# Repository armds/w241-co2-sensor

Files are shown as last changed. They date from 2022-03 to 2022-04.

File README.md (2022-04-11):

# Intro
This is the repository for code and documents for the sensor we built for our w241 - Causal Inference class project, Spring 2022.

It should give you enough information to build one of these sensors should you so desire.

# Components required

## Arduino components

- [Sparkfun Qwiic Pro Micro USB-C](https://www.sparkfun.com/products/15795?_ga=2.264082766.31748102.1649701746-416199447.1644960318)  This is the Arduino mainboard we used.  Other boards can be used instead, but the CAD expects this one and the other boards are Qwiic connectors so it should support this.
- [Sparkfun CCS811/BME280 (Qwiic) Environmental Combo Breakout](https://www.sparkfun.com/products/14348?_ga=2.264082766.31748102.1649701746-416199447.1644960318) This board is the heart of the sensor.  Once calibrated (see notes below) it will measure temperature, humidity, air pressure, CO2 and TVOC.
- [SparkFun Real Time Clock Module](https://www.sparkfun.com/products/14558?_ga=2.62422382.31748102.1649701746-416199447.1644960318)  This chip is required to have a continuous sense of time.  Without it the device's only sense is seconds since power cycle.  Nominally that would work for an experiment, but in practice the power tends to flicker and cause frequent resets.
- [Sparkfun Qwiic OpenLog](https://www.sparkfun.com/products/15164?_ga=2.264082766.31748102.1649701746-416199447.1644960318)  This is required if you want to operate your device away from computer and persist the data.  Hypohtetically you could instead use a wifi card and configure it write to the cloud, but we wanted to use it in locations remote from where it was developed so could not guarenee connectivity.

## Other components
- [Battery Pack](https://www.amazon.com/gp/product/B08T8TDS8S)  The device does not care what its power supply is.  It can be powered off a computer, or any portable USB power supply. That said the CAD provided exactly matches these batteries, and using any other will require a new case.

- [USB cables ](https://www.amazon.com/gp/product/B096VYVR17) Again any USB cables can be used.  Our battery only has Micro USB and USB A, and the CPU needs USB-C.  With the case space constraints we went with these, and again, the CAD expects it.

- [3x Qwiic cables](https://www.sparkfun.com/products/17260) These aren't special, you just need 3 Qwiic cables per sensor, get what works for you.

# CAD for case and cover

If you are using all the same parts as us, you can use the STL files in the *Case STL* directory to just print them.  Hopefully they work for you.  The spaces are intentionally designed to be a tight fit for the cards, and they are all subtily different shapes so will only work exactly in the configuration shown below.  They may be quite snug, so be firm but gentile pushing them in.

Its also possible that the fit between case and cover is either too loose or too tight.  For loose (our case) use a few pieces of thin tape to fill the gaps so they are snug.

If they really don't fit, or you want to change the configuration or battery, the [Onshape CAD Project](https://cad.onshape.com/documents/a2fdd6d62e2931dea2922d15/w/b632312d6c9ec3a2012bce3f/e/c36cc9c0a84920fe10cffbab) is public. You will likely need to make an Onshape account, and then can copy the files and edit them.

# Assembly
Blow are what they should look like open, with cards installed (yes they have to go in these spots!), and with the covers on.  They are fairly inconsipcuous with covers, but the lights inside have occasionally cought folks' attention.

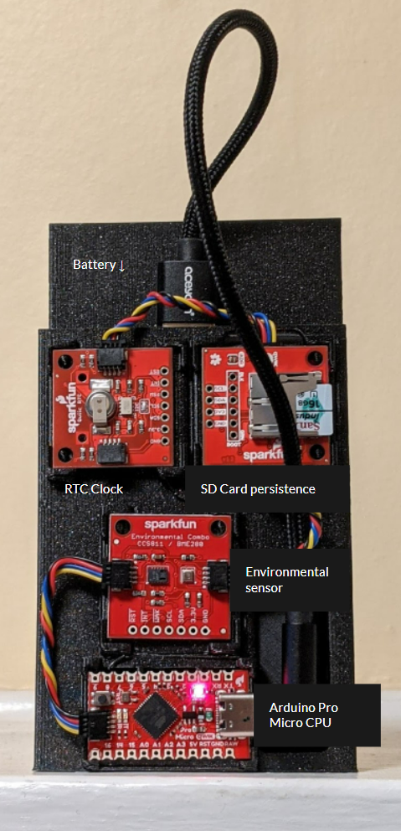
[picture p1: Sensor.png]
Image of case with cards properlly aranged


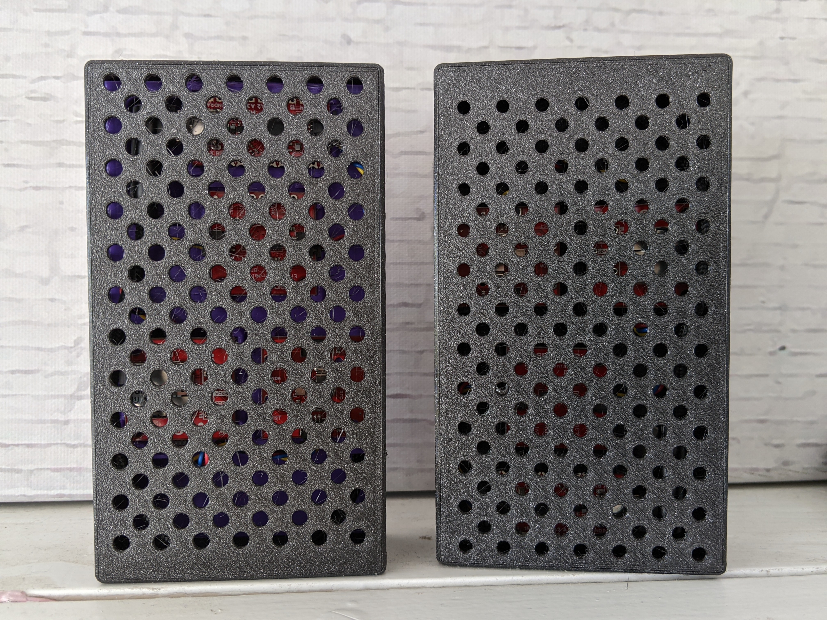
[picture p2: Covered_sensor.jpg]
Sensors with covers on


# Code for device

The code for the devices is in this repository in the *timed_sensor* directory.  The *base_sensor* will give you an earlier version that didn't have a persistant clock.

Use any tutorial on using the Arduino IDE to install the code on the device.  Its fairly simple, so SparkFun's basic tutorial is fine.

Code in this repo is based on the example code provided by SparkFun for each card.  They are a good reference for understanding it for modification.

## Time setting

One important issue is setting the clock chip.  The way it is set is when you push the code to the device it will set the device's time to the time at which the IDE was started.   So if you take 10 minutes from start to upload your clock will be off by that amount.  So get your code perfect, restart the IDE, and push.  Do this cycle for each device, and know they will be off by some degree due to the time this delay.  Sorry for the hassle, it is regretable!

Additionally our devices were built in one time zone, and deployed in another, so there is a 3 hour timezone correction built into the code, which may not be needed for all applications.

# Caviats for use

There are a few execution requirements to ensure you get an accurate atospheric measurements.

## Sensor Calibration

The first caveat is the sensors need to be calibrated at rest in a stable environment before starting to collect data.  The Environment chip has both the temperature sensor and the air sensor in close proximity.  At operating temperature the environmental chip can generate significant heat (up to 15 deg).  The temperature is one of the inputs for the CO2 calibration, so this temperature increase will make the measurements in accurate.  To compensate for this the device records its temperature at power up, and after 20 minutes will take the accumulated temperature change and subtract that from all subsequent measurements for calibration. In addition the plastic of the case and the battery can hold heat that messes this up.

This means for best performance when not in use you should to hold all devices in the same place, ideally not indoors, so the residual temperature is close to outdoors.  Additionally you should plug them in 20 minutes in advance, and keep them in a stabile temperature location.  So that that calibration constant is not picking up additional effects. 

Best practice would be to keep them outside, or in a cool garage, plug them in a half hour before you will deploy them, and minimize heat accumulation en route.

## Operating limits

These are prototype devices so are not environmentally secured.  In particular they are not robust to rain, so need to be placed  someplace under shelter.  Additionally direct sunlight can increase both measured temperature and CO2.  So both devices should be deployed with the same sun exposure, ideally shaddowed.

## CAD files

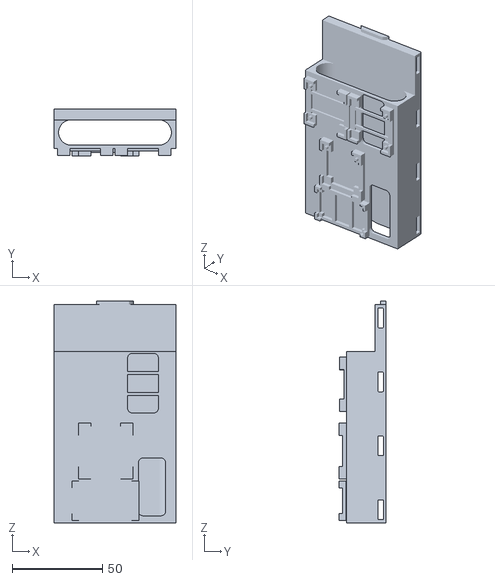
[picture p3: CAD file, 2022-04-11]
Case STLs/Battery and card holder.stl
67.5 x 26.0 x 123.0

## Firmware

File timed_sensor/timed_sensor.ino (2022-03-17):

/******************************************************************************
  Reads information from an evironmental sensor and writes an hourly csv file
  with environmental data.

  Boards expected:

  - Sparkfun Qwiic Pro Micro USB-C
  - Sparkfun CCS811/BME280 (Qwiic) Environmental Combo Breakout
  - Sparkfun Qwiic OpenLog
  - SparkFun Real Time Clock Module

  Libraries required:
   http://librarymanager/All#SparkFun_CCS811
   http://librarymanager/All#SparkFunBME280
   https://www.arduinolibraries.info/libraries/spark-fun-qwiic-open-log
   http://librarymanager/All#SparkFun_RV1805

 Author: Anne Marshal 
 Copyright: 2022
******************************************************************************/
#include <Wire.h>

#include "SparkFunCCS811.h" 
#include "SparkFunBME280.h"
#include "SparkFun_Qwiic_OpenLog_Arduino_Library.h"
#include "SparkFun_RV1805.h"

#define CCS811_ADDR 0x5B //Default I2C Address for the sensor
//#define CCS811_ADDR 0x5A //Alternate I2C Address

CCS811 myCCS811(CCS811_ADDR);
BME280 myBME280;
OpenLog myLog; //Create instance
RV1805 rtc;
OpenLog dataLog;

float tempCorrectionC = 0;
float tempCorrectionF = 0;
boolean correctionSet = false;
float startTempC;
float startTempF;

// How long to wait for temperature stabilization for correction term, normally 20
float delayMinutes = 20;

// sleep tolerance, how old a calibration use stamp can be for us to still use it.
float tolMinutes = 10;

// Name of calibration timestamp file
String calibrationTimeStampFile = "calstamp.txt";

// set this to either B or W depending on which sensor is being written to
// is only used for output CSV filenames
char sensorId = 'P';

// if we need to set the clock chip, this will set it to the time the IDE started
// then add 3 hours to adjust to EST time.  Don't do this after 9pm thought, 'cause its not smart!
// unless the chip has crashed for a while, it should seldom need to have the clock set.
boolean setClock = false;

// desired interval between samples in seconds
unsigned int secsBetweenSamples = 5;

// interval between calibration file writes
unsigned int secsBetweenCalibWrites = 120;


// string buffers like to be global, because memory is a thing
char fCorr[10];
char cCorr[10];
char calibuf[30];
char calibuf2[30];     

// Globalize frequently used vars for faster loops
unsigned int loopStartTime;
String currentTime;

   
void setup()
{
  Serial.begin(9600);

  Wire.begin(); //Initialize I2C
  myLog.begin(); //Open connection to OpenLog (no pun intended)

  // initialize clock
   if (rtc.begin() == false) {
    Serial.println("Something went wrong, check wiring");
  }

  //Use the time from the Arduino compiler (build time) to set the RTC
  //Keep in mind that Arduino does not get the new compiler time every time it compiles.
  //to ensure the proper time is loaded, open up a fresh version of the IDE and load the sketch.
  rtc.set24Hour();
  if (setClock) {
    if (rtc.setToCompilerTime() == false) {
      Serial.println("Something went wrong setting the time");
    }

    rtc.updateTime();
    // correct to put it in EST not PST
    int hrs = rtc.getHours();
    int day = rtc.getDate();
    int EST = hrs+3;
    if (EST > 23) {
      EST = EST - 24;
      day = day +1;
    }
    rtc.setHours(EST);
    rtc.setDate(day);
  }
  
  // set up environment sensor
   if (myCCS811.begin() == false)
  {
    Serial.print("CCS811 error. Please check wiring. Freezing...");
    while (1)
      ;
  }

  //This begins the CCS811 sensor and prints error status of .beginWithStatus()
  CCS811Core::CCS811_Status_e returnCode = myCCS811.beginWithStatus();
  Serial.print("CCS811 begin exited with: ");
  //Pass the error code to a function to print the results
  Serial.print(myCCS811.statusString(returnCode));
  Serial.println();
  
  myCCS811.setRefResistance(9950);

  //Initialize BME280
  if (myBME280.beginI2C() == false) //Begin communication over I2C
  {
    Serial.println("The sensor did not respond. Please check wiring.");
    while(1); //Freeze
  }

  myBME280.settings.runMode = 3; //Normal mode
  myBME280.settings.tStandby = 0;
  myBME280.settings.filter = 4;
  myBME280.settings.tempOverSample = 5;
  myBME280.settings.pressOverSample = 5;
  myBME280.settings.humidOverSample = 5;

  
  delay(10);  //Make sure sensor had enough time to turn on. BME280 requires 2ms to start up.
  byte id = myBME280.begin(); //Returns ID of 0x60 if successful
  if (id != 0x60)
  {
    Serial.println("Problem with BME280");
  }
  else
  {
   // if last run time > 
    startTempC = myBME280.readTempC();
    startTempF = myBME280.readTempF();
    Serial.print("BME280 online Initial temperature(C):" );
    Serial.println(startTempC);
  }
}

void loop()
{
  loopStartTime = millis();
  
  if (rtc.updateTime() == false) //Updates the time variables from RTC
  {
    Serial.print("RTC failed to update");
  }
  currentTime = rtc.stringTime();

  // if the current logging csv file does not exist, intitalize it with the header row
  String currentLogFileName = getCurrentLogFileName();
  if (myLog.size(currentLogFileName) <1){
    Serial.print(currentTime);
    Serial.print("\tInitializing logfile: ");
    Serial.println(currentLogFileName);
    myLog.append(currentLogFileName);
    myLog.println("Time,TempC,TempF,Humid%,Corr TempC,Corr TempF,Press mbar,CO2 ppm,TVOC ppb,RunTime,Validity");
    myLog.syncFile();
  }

  //Check to see if environmental data is ready with .dataAvailable()
  if (myCCS811.dataAvailable())
  {

    // outputString is the log message you'll see on the monitor
    String outputString ="";

    //dataLogString is the comma delimited data written to the hourly csv files
    String dataLogString ="";
    
    //read the sensor and calculate the results.
    myCCS811.readAlgorithmResults();

    float BMEtempC = myBME280.readTempC();
    float BMEtempF = myBME280.readTempF();
    float BMEhumid = myBME280.readFloatHumidity();

    //once we have the base read, we can work out if we have the correction parameters we need yet
    if (!correctionSet) {
      // we've waited long enough, and not picked it up from a file so... do the calculation
      if( millis() > delayMinutes * 60 * 1000 ){
        // calculate the temperature differential of the chip warming up.  Device should be held
        // and environment with a stable temperature for the first delayMinutes from power up.
        // delay of 20 minutes recommended
        tempCorrectionC = BMEtempC-startTempC;
        tempCorrectionF = BMEtempF-startTempF;
        outputString += "Found Temperature correction of ";
        outputString += tempCorrectionC; 
        outputString += " at time ";
        outputString += currentTime;
        outputString += "\n";
        correctionSet = true;
      } 
      else if ( myLog.size(calibrationTimeStampFile) > -1){
        // check for logged calibration, if recent enough will be used for corrections
        myLog.read(calibuf,30,calibrationTimeStampFile);

        // arudino C is limited, so we need to deal with the input as string buffers :(
        char buff[2];
        //year
        buff[0] = calibuf[0];
        buff[1] = calibuf[1];
        int caliyear = atoi(buff);

        //month
        buff[0] = calibuf[3];
        buff[1] = calibuf[4];
        int calimonth = atoi(buff);
        
        //day
        buff[0] = calibuf[6];
        buff[1] = calibuf[7];
        int caliday = atoi(buff);
        //hour
        buff[0] = calibuf[9];
        buff[1] = calibuf[10];
        int calihour = atoi(buff);
        //minute
        buff[0] = calibuf[12];
        buff[1] = calibuf[13];
        int calimin = atoi(buff);  

        // and it REALLY can't deal with floats.  I appologize to any reader that this is what it 
        // is apparently adruino thinks this is best?
        
        char fbuff[6];
        //cCalibration
        fbuff[0] = calibuf[15];
        fbuff[1] = calibuf[16];
        fbuff[2] = calibuf[17];
        fbuff[3] = calibuf[18];
        fbuff[4] = calibuf[19];
        fbuff[5] = calibuf[20];
        fbuff[6] = calibuf[21];
        fbuff[7] = calibuf[22];
        fbuff[8] = ' ';
        fbuff[9] = ' ';
        float caliC = atof(fbuff);

        //cCalibration
        fbuff[0] = calibuf[24];
        fbuff[1] = calibuf[25];
        fbuff[2] = calibuf[26];
        fbuff[3] = calibuf[27];
        fbuff[4] = calibuf[28];
        fbuff[5] = calibuf[29];
        fbuff[6] = calibuf[30];
        fbuff[7] = calibuf[31];
        fbuff[8] = ' ';
        fbuff[9] = ' ';
        float caliF = atof(fbuff);

        if (caliyear == rtc.getYear() &&
            calimonth == rtc.getMonth() &&
            caliday == rtc.getDate() &&
            ((calihour == rtc.getHours() && (rtc.getMinutes() - calimin < tolMinutes)) ||
              (calihour +1 == rtc.getHours() && (rtc.getMinutes()+60 - calimin < tolMinutes)))) {
                sprintf(calibuf2, "%02d %02d %02d %02d %02d ", 
                        caliyear,calimonth,
                        caliday,calihour, calimin);
                Serial.print("Reusing calibration from file: ");
                Serial.print(calibuf2);
                Serial.print(caliC);
                Serial.print(" ");
                Serial.println(caliF);
                tempCorrectionC = caliC;
                tempCorrectionF = caliF;
                correctionSet = true;
        } 
      }
    }
   
    dataLogString += currentTime;
    dataLogString += ",";
    dataLogString += BMEtempC;
    dataLogString += ",";
    dataLogString += BMEtempF;
    dataLogString += ",";
    dataLogString += BMEhumid;
    dataLogString += ",";
    dataLogString += BMEtempC-tempCorrectionC;
    dataLogString += ",";
    dataLogString += BMEtempF-tempCorrectionF;
    dataLogString += ",";
    
    //This sends the temperature data to the CCS811 to calibrate the sensor readings
    myCCS811.setEnvironmentalData(BMEhumid, BMEtempC-tempCorrectionC);
    
    outputString += "Time\t";
    outputString += currentTime;

    
    outputString +=("\tcorrected temp\t");
    outputString +=(BMEtempC-tempCorrectionC);
    outputString +=("C");

    outputString +=("\t");
    outputString +=(BMEtempF-tempCorrectionF);
    outputString +=("F\t");
    
    outputString +=" CO2\t";
    //Returns calculated CO2 reading
    outputString +=myCCS811.getCO2();
    
    dataLogString += myCCS811.getCO2();
    dataLogString += ",";
    
    outputString +="ppm\t tVOC\t";
    //Returns calculated TVOC reading
    outputString += myCCS811.getTVOC();
    outputString += "ppb\t";
    outputString += printRunTime(loopStartTime);
    
    dataLogString += myCCS811.getTVOC();
    dataLogString += ",";  
    dataLogString += printRunTime(loopStartTime);
   
    Serial.println(outputString);
    myLog.append(currentLogFileName);
    myLog.println(dataLogString);
    myLog.syncFile();
          
    // write out the latest calibration time and value, so we can reuse at restart
    // only do this once a minute
    /*Serial.print(loopStartTime % (secsBetweenCalibWrites *1000));
    Serial.print(" vs ");
    Serial.println(secsBetweenSamples*1000);
    */
    if (correctionSet & (loopStartTime % (secsBetweenCalibWrites *1000) <= secsBetweenSamples*1000)) {
      if (myLog.size(calibrationTimeStampFile) > -1) {
        myLog.removeFile(calibrationTimeStampFile);
      }
      myLog.append(calibrationTimeStampFile);

    // arudino sprintf can't do floats because ¯\_(ツ)_/¯
      dtostrf(tempCorrectionC,8,1,cCorr);
      dtostrf(tempCorrectionF,8,1,fCorr);

      sprintf(calibuf, "%02d %02d %02d %02d %02d %s %s", 
              rtc.getYear(),rtc.getMonth(),
              rtc.getDate(),rtc.getHours(),rtc.getMinutes(),
              cCorr, fCorr);
      myLog.println(calibuf);
      myLog.syncFile();
      Serial.print("Wrote calibration file: ");
      Serial.println(calibuf);
    }      

  }
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
